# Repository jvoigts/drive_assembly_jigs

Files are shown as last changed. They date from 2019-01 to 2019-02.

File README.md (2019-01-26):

# An easy-to-assemble, robust, and ultralight drive implant for chronic tetrode recordings in freely moving animals

Licensed under CERN OHL v.1.2

The basic design uses polymicro fused silica tubes as free standing shuttle tubes to avoid having to use bent guide tubes.
The shuttles are 3d printed or milled teflon sliding in slots in a 3d printed body, moved by captive custom screws.
The straight bottom guide tube array can either be milled, or made in the classical fashion from bundled and cut polymide tubes, or even 3d printed in a ultra-high precision process(?).

The captive custom drive screws (currently M0.6 for mouse and M0.8 for rat/shrew) incorporate a captive guide feature under the screw head that is held by epoxy or dental acrylic in a well at the top of the drive after the screws have been inserted into the drive body, ensuring minimal hysteresis and very quick assembly. The bottom of the screws are captive in a hole at the drive body base giving them addiitonal stability.

### License:

Copyright Jakob Voigts 2017.
This documentation describes Open Hardware and is licensed under the CERN OHL v. 1.2.
You may redistribute and modify this documentation under the terms of the CERN OHL v.1.2. (http://ohwr.org/cernohl). 
This documentation is distributed WITHOUT ANY EXPRESS OR IMPLIED WARRANTY, INCLUDING OF MERCHANTABILITY, SATISFACTORY QUALITY AND FITNESS FOR A PARTICULAR PURPOSE. Please see the CERN OHL v.1.2 for applicable conditions.

### Current variants:
- Mouse: 16 drives
- Rat/shrew: 64 drives

EIB mounts to ring on drive:
- Mouse: 8.56 outer diam radius 15.94 inner diameter.
- Rat/shrew: 40mm diameter OD on drive body mount.

to be used with flat SERDES 64/128ch headstage.

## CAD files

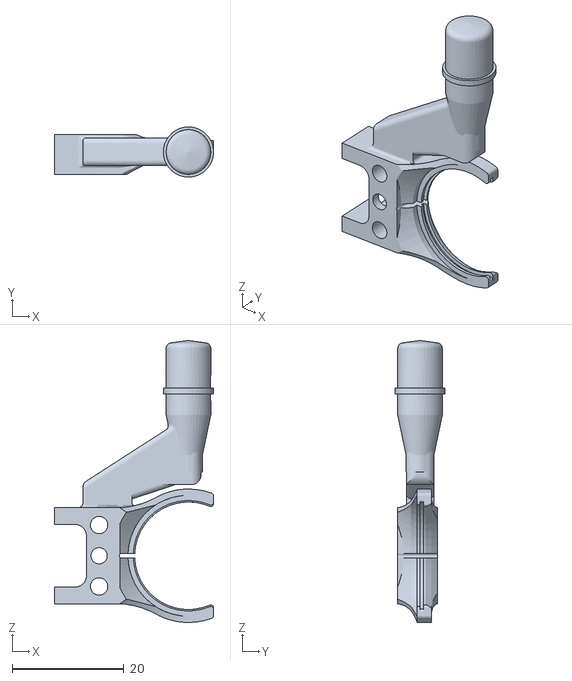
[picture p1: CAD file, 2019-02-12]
assembly_jig_mouse/drive_holder_bottom.STL
28.5 x 8.99 x 50.5

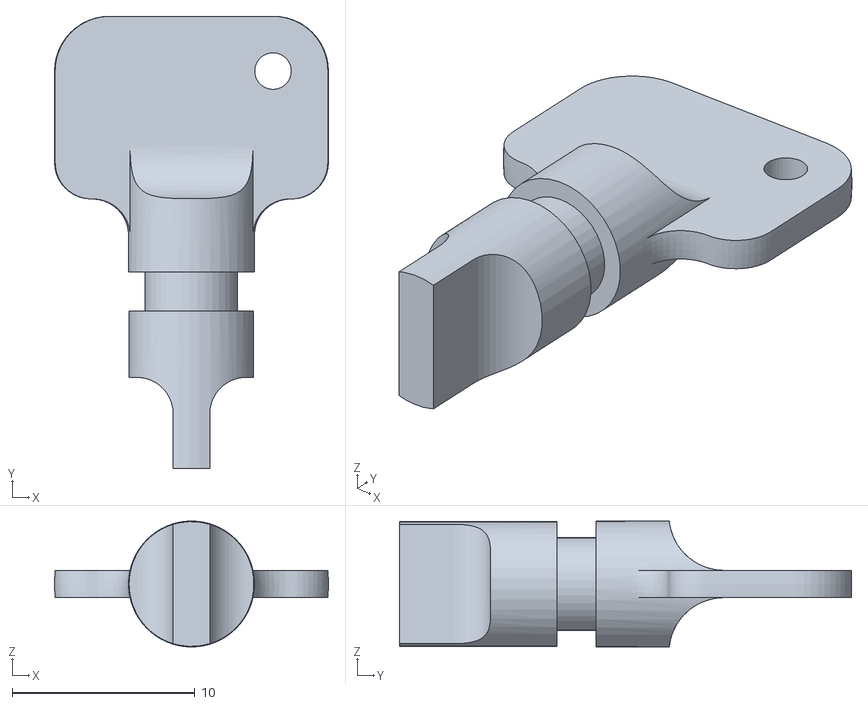
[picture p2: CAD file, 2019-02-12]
assembly_jig_mouse/eib_holder_inner.STL
15.0 x 24.8 x 6.89

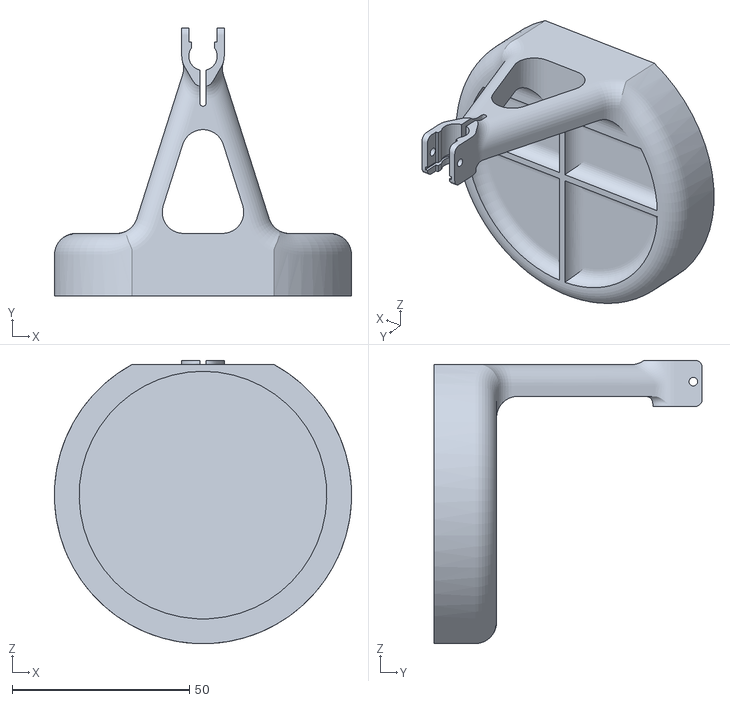
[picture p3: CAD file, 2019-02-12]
assembly_jig_mouse/jig_base_big_rat.STL
83.8 x 75.7 x 79.9

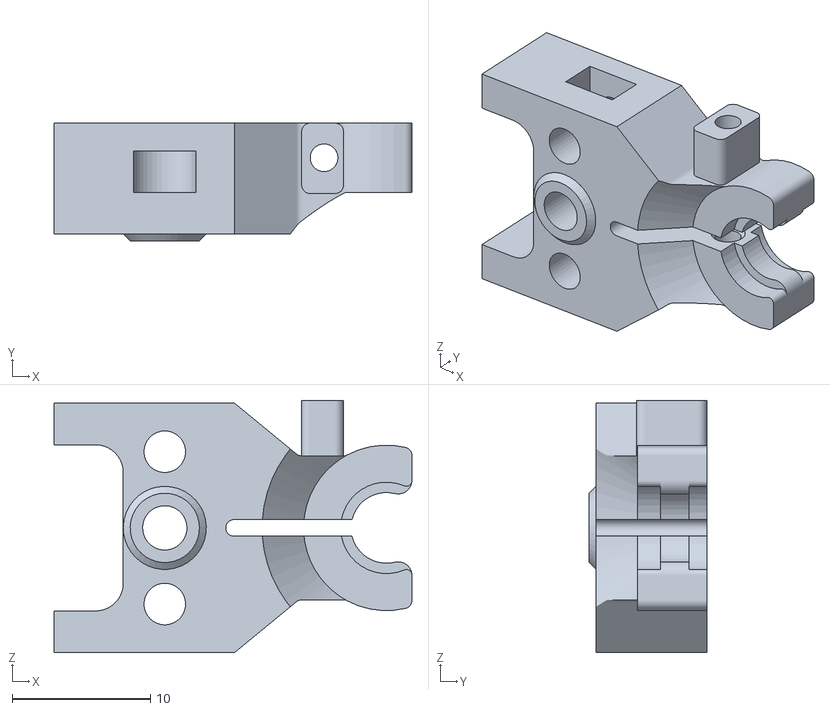
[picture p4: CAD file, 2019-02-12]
assembly_jig_mouse/eib_holder_top.STL
25.9 x 8.50 x 18.2

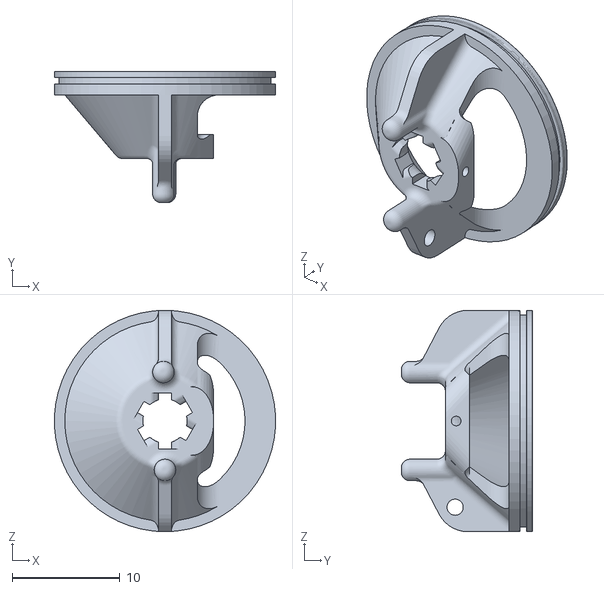
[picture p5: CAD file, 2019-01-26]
assembly_jig_mouse/drive_holder_inner.STL
20.5 x 12.2 x 20.5

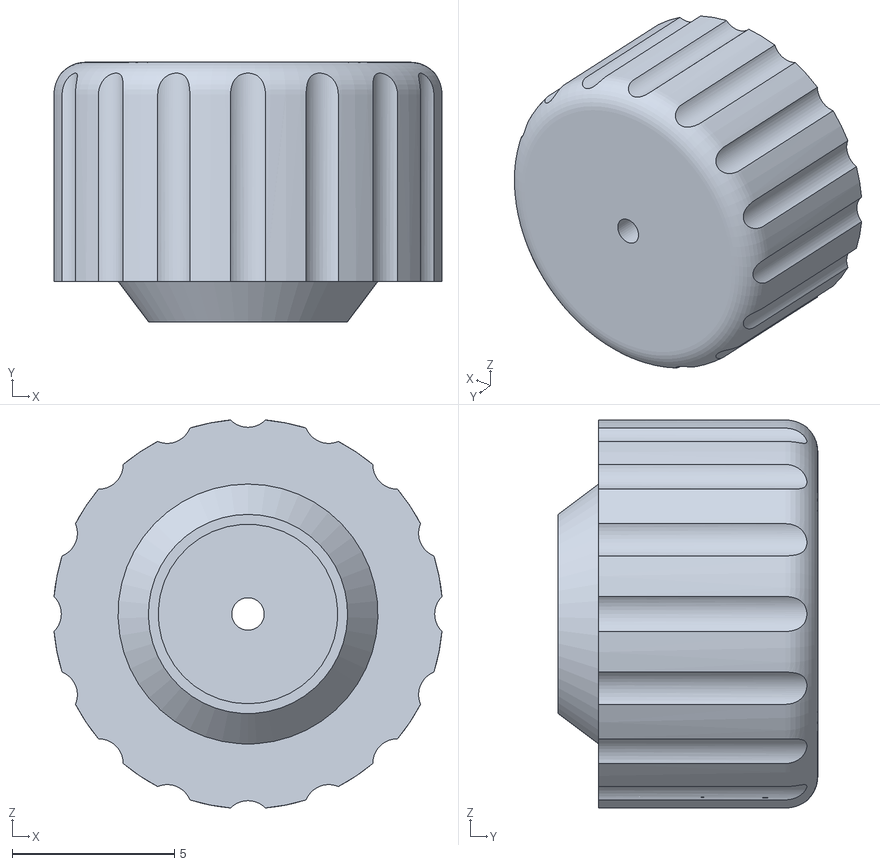
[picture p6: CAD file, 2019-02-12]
assembly_jig_mouse/screw_thumbwheel.STL
12.0 x 8.00 x 12.0

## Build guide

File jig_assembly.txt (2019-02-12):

Assembly jigs:

The jigs are made up of various 3d-printed components, and a few screws and dowels.
Some components can be printed with relatively low-resolution processes (ideally sintered nylon powder at !0.12mm layer height, but high quality fused plastic could also work), while some required medium-resolution printing (Multijet Modeling or Stereolithography, with around 0.03mm layer thickness).

For example, the low quality parts can be printed with the Shapeways versatile plastic process, while the medium quality parts can be printed with smooth fine detail plastic.

The components are:
 
1 -Base (low quality) - the base everything else sits on. Shared bwteeen the rat and the mouse design. All other componets differ between the two variants.

2 -Outer drive holder (medium quality*) - connects to the base and holds the drive holder.

3 -Inner drive holder (medium quality*) - sits inside the outer drive holder and directly holds the drive body, allowing it to rotate around its major axis.

4 -Inner EIB holder (medium quality*) - holds the EIB, allowing it to rotate. This part may have to be customized to fit the desired type of EIB.

5 -Outer EIB holder (medium quality*) - Holds the inner EIB holder.

6- Manual adjustment knob (low quality) to make adjusting the long screw easier - hand-adjustible screws can be used alternatively, or tools can be used ot adjust mechnaism distance.

* for the rat variant, all parts can be printed with a lower quality process in some cases.

The outer EIB and drive holders form a linear slide that allows adjustments of their distance to each other. This slide is formed by two dowels and a screw.

BOM (part numbers are Mcmaster-Carr):

both variants
4x parts medium quality 3d printing, separate for rat and mouse drives, the rat variant has less stringent resolution requirements.
1x part low quality 3d printing.
1x lead disc, 1/2" Thick, 2-3/4" OD, #	90385K22 $19
1x M2 screw and nut for clamping drive holder to base. # 	91292A032 , $6 for 10
1x plastics compatible lubricant for bearing surfaces (optional) 

Mouse variant
2x M3 40mm dowels, # 91585A426, $10 for 25
1x M3 40mm screw, fully threaded, # 	91292A024, $ 3 for 25
1x M3 washer (for gluing against top slide as retainer), # 	90965A130, $3 for 100
1x M1 screw (for holding in drive especially securely, optional)

Rat variant
2x M5 70mm dowels
1x M5 70mm screw, fully threaded
2x M3x15mm screws for holding drive to drive holder
1x M2xXXmm screw, non-threaded below screw head, to make IEB holder pin
1x M2 nut for manual adjustment, either knurled, or wing nut.

Assembling the assembly jigs: 

- Glue lead disc into base with epoxy, and cover entire base surface with epoxy, so that no lead remains exposed.
- The dowels should slide freely trough the lower side of the slide / trough the outher drive holder, and the adjustment screw should freely slide trough the hold in the outer EIB holder. If not, these holes can be drilled out.
- If needed, the dowels can be glued into one side of the linear slide by using the provided glue pockets, and similarly, threads for the adjustment screw can be formed by lightly oiling the screw, turning it trough the lower part of the slide (the outer drive holder) and the filling the provided cavity with epoxy.
- Insert lower EIB holder into the base, and add clamping screw and nut. 
- (For the mouse variant) insert inner EIB holder into outer EIB holder and add clamping screw and nut.
- Glue clamping nuts to the 3d printed parts with epoxy in their clamped state.
- Insert slide with EIB holder into the outer drive holder and verify proper function of the distance adjustment.
